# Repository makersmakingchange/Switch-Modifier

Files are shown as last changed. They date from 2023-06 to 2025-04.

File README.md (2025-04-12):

# Switch Modifier
## Overview

The switch modifier is an affordable accessibility device that enables specific switch output functions. With the provided Arduino code, the switch modifier outputs a momentary switch signal for a specific hold duration, in response to a digital input signal. Regardless of the duration of the input signal, the output can be set to any duration from 20 to 500 milliseconds. Manually turning a potentiometer allows for adjustment in output duration.

## Usage

With the provided Arduino code, the intended usage is for applications that require fast, short duration switch activation, where the user’s motor control is too slow to achieve such movement. To achieve multiple switch activations, the user must release the input switch first before activating it again. Minor adjustments to the code may provide for longer output durations, or latching functionality.

## Disclaimer
**Construction, use and modification of this device is the responsibility of the end user. The Stan Cassidy Centre for Rehabilitation and its employees are not responsible for any damages or harm as a result of the construction or use of this device.**

## Build Instructions

#### Tools Required

- Soldering Iron
- Screw Driver
- Wire Cutters / wire strippers
- Super Glue

#### 3D Printing

The lid and the base are printed face up with no supports. The middle piece is printed in its intended usage orientation (lettering upright) and will require supports in the bottom battery compartment, and port holes in the walls. The original box was printed on a Raise3D N2 printer using PLA. Speed printing is approximately 7.5 hours and high quality is approximately 18.5 hours.

### Assembling the Circuit

Take care in the placement of the electronics on the proto board to allow for everything to fit. Only attach the back end of the nano controller up to pins D2 and A7 (inclusive). The remaining portion of the controller will overhang and rest on the support structure. Ensure the nano controller will line up with the access port on the side wall of the 3D printed box.
Please refer to the following diagram for assembling the rest of the circuit.
Note: Do not solder the battery holder wires on until the 3D printed box is ready and the wires can be passed through the access hole.

### Assembling the Box

1. Remove all 3D printed supports from the middle section of the box.
2. Feed the battery holder wires through the access hole and mount it in the bottom compartment using two M2x6 screws.
3. Mount the assembled proto board to the standoffs in the upper compartment using two M2x6 screws.
4. Solder the battery wires to the appropriate locations on the proto board. Ensure not to melt the plastic box.
5. Mount the auxiliary mono jacks in the appropriate port holes in the walls of the box.
6. Mount the ON/OFF switch in the remaining port hole in the wall of the box using super glue. Ensure not to glue the switch stuck in the ON or OFF position.
7. Attach the lid of the box using four M2x20 screws. Ensure not to over torque the screws and damage the lid. Also, ensure that no wires are pinched between the lid and the walls of the box.
8. Insert four AA batteries (not included in list of materials) into the battery holder.
9. Attach the base of the box using found M2x20 screws. Ensure not to over torque the screws and damage the base.

## License
<!--- LICENSE Choose an appropriate license. We recommend an open-source hardware compatible license. --->
Everything needed or used to design, make, test, or prepare the Switch Modifier is licensed under the CERN 2.0 Weakly Reciprocal license <https://ohwr.org/project/cernohl/wikis/Documents/CERN-OHL-version-2> (CERN-OHL-W).

Accompanying material such as instruction manuals, videos, and other copyrightable works that are useful but not necessary to design, make, test, or prepare the Switch Modifier are published under a Creative Commons Attribution-ShareAlike 4.0 license <https://creativecommons.org/licenses/by-sa/4.0/> (CC BY-SA 4.0).

## Attribution 
<!--- ATTRIBUTION Include any information related to the development of the design. This may include who identified the initial challenge, who contributed to the design --->
The Lift Switch was designed by the Rehabilitation Engineering Department at Horizon Health's Stan Cassidy Centre for Rehabilitation (SCCR).  

The documentation template was created by Makers Making Change and is used under a CC BY-SA 4.0 license. It is available at the following link: https://github.com/makersmakingchange/OpenAT-Template

---

<!-- ABOUT MMC START -->
## About Makers Making Change
[Makers Making Change Logo](https://www.makersmakingchange.com/)

Makers Making Change is a program of [Neil Squire](https://www.neilsquire.ca/), a Canadian non-profit that uses technology, knowledge, and passion to empower people with disabilities.

Makers Making Change leverages the capacity of community based Makers, Disability Professionals and Volunteers to develop and deliver affordable Open Source Assistive Technologies.

 - Website: [www.MakersMakingChange.com](https://www.makersmakingchange.com/)
 - GitHub: [makersmakingchange](https://github.com/makersmakingchange)
 - Bluesky: [@makersmakingchange.bsky.social](https://bsky.app/profile/makersmakingchange.bsky.social)
 - Instagram: [@makersmakingchange](https://www.instagram.com/makersmakingchange)
 - Facebook: [makersmakechange](https://www.facebook.com/makersmakechange)
 - LinkedIn: [Neil Squire Society](https://www.linkedin.com/company/neil-squire-society/)
 - Thingiverse: [makersmakingchange](https://www.thingiverse.com/makersmakingchange/about)
 - Printables: [MakersMakingChange](https://www.printables.com/@MakersMakingChange)

### Contact Us
For technical questions, to get involved, or to share your experience we encourage you to [visit our website](https://www.makersmakingchange.com/) or [contact us](https://www.makersmakingchange.com/s/contact).
<!-- ABOUT MMC END -->

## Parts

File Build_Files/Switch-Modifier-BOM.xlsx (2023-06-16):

Switch Modifier BOM
Arduino Nano (elegoo) | 1 | 5.883333333 | 5.883333333 | https://www.amazon.ca/Arduino-ELEGOO-ATmega328P-Compatible-Without/dp/B071NMD14Y?hvadid=208380738475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
Aux ports | 2 | 1.68 | 3.36 | https://www.digikey.ca/products/en?keywords=CP1-3533NG-ND
Relays | 1 | 7.34 | 7.34 | https://www.digikey.ca/product-detail/en/omron-electronics-inc-emc-div/G6E-134P-ST-US-DC5/Z830-ND/127440?pcrid=267468162425&pkw=&pmt=b&pdv=c&productid=&slid=
3D printed box (PLA) | 1 | 3 | 3 | Rehab Eng Supplies
Wires/Solder/Heat shrink | 1 | 0.5 | 0.5 | Misc supplies
Battery Holder 4xAA | 1 | 2.55 | 2.55 | https://www.digikey.ca/product-detail/en/keystone-electronics/2478/36-2478-ND/303823
SPST Switch | 1 | 1.65 | 1.65 | https://www.digikey.ca/product-detail/en/cw-industries/GF-123-3011/CWI334-ND/4089772
Fuse Holder | 1 | 0.95 | 0.95 | https://www.digikey.ca/product-detail/en/keystone-electronics/4527/36-4527-ND/8397
Fuse 250 mA | 1 | 0.3 | 0.3 | https://www.digikey.ca/product-detail/en/bel-fuse-inc/5MF-250-R/507-1257-ND/1009029
Project Board | 1 | 4.22 | 4.22 | https://www.digikey.ca/product-detail/en/adafruit-industries-llc/1608/1528-1101-ND/5154676
10kOhm Resistor | 1 | 0.15 | 0.15 | https://www.digikey.ca/product-detail/en/stackpole-electronics-inc/CF14JT10K0/CF14JT10K0CT-ND/1830374
Potentiometer | 1 | 0.57 | 0.57 | https://www.digikey.ca/product-detail/en/panasonic-electronic-components/EVN-DJAA03B55/DJA55CT-ND/274655
M2*6 Machine Screw | 4 | 0.06 | 0.24 | https://www.mcmaster.com/machine-screws
M2*20 Maching Screw | 4 | 0.06 | 0.24 | https://www.mcmaster.com/machine-screws
 |  |  | 30.95333333
Notes:
You can by a kit of small machine screws on amazon instead of individual sizes.
I used glue to mount the SPST ON/OFF switch.

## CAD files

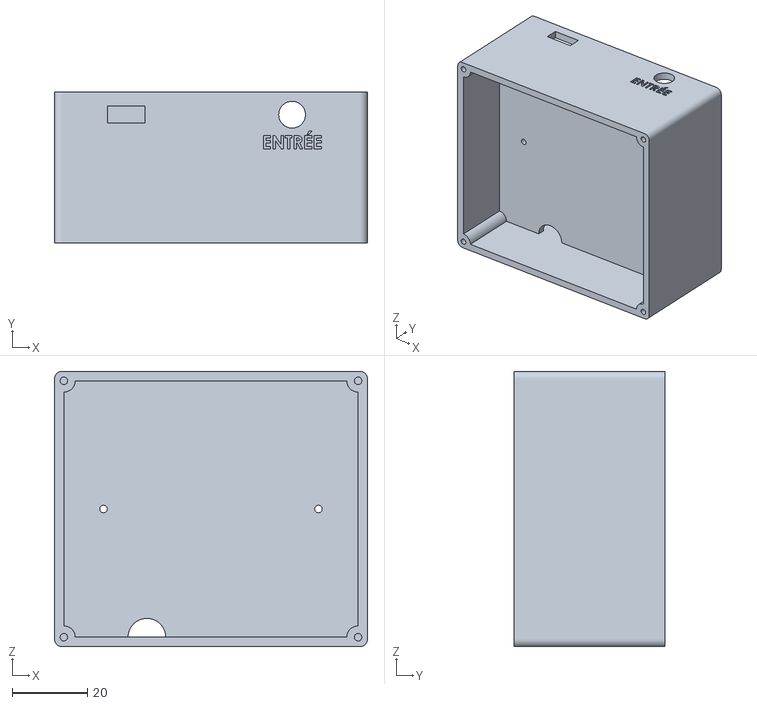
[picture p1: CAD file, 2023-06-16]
Build_Files/Electronics-Box-Switch-Modifier.STL
83.0 x 40.0 x 73.0

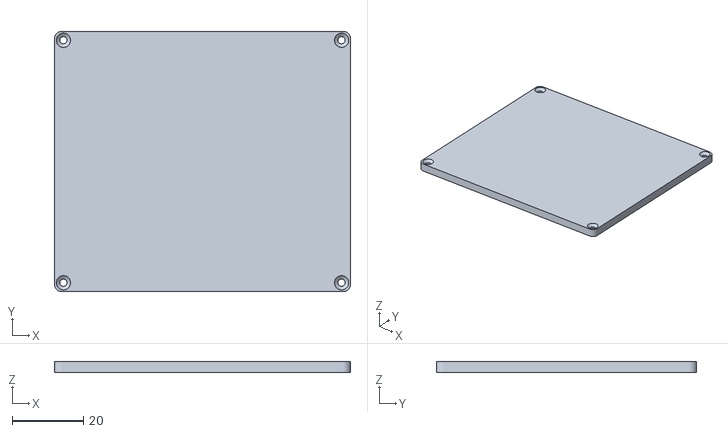
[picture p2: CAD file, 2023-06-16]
Build_Files/Base-Electronics-Box-Switch-Modifier.STL
83.0 x 73.0 x 3.00

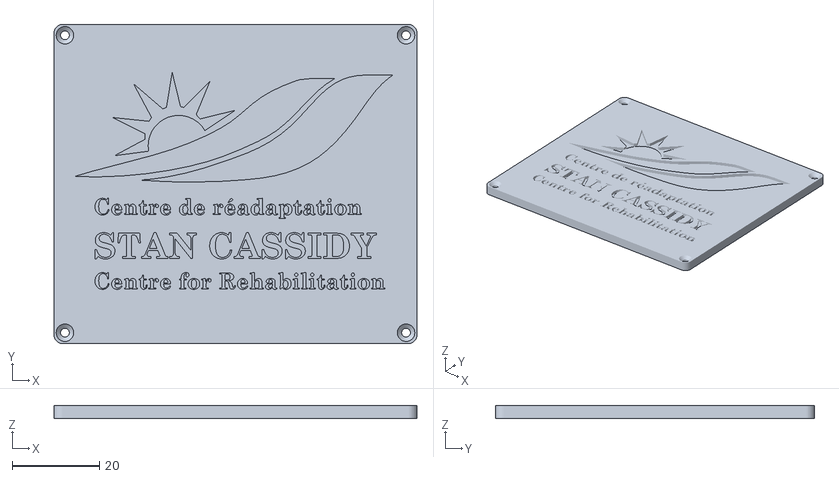
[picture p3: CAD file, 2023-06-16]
Build_Files/Lid-Electronics-Box-Switch-Modifier.STL
83.0 x 73.0 x 3.00

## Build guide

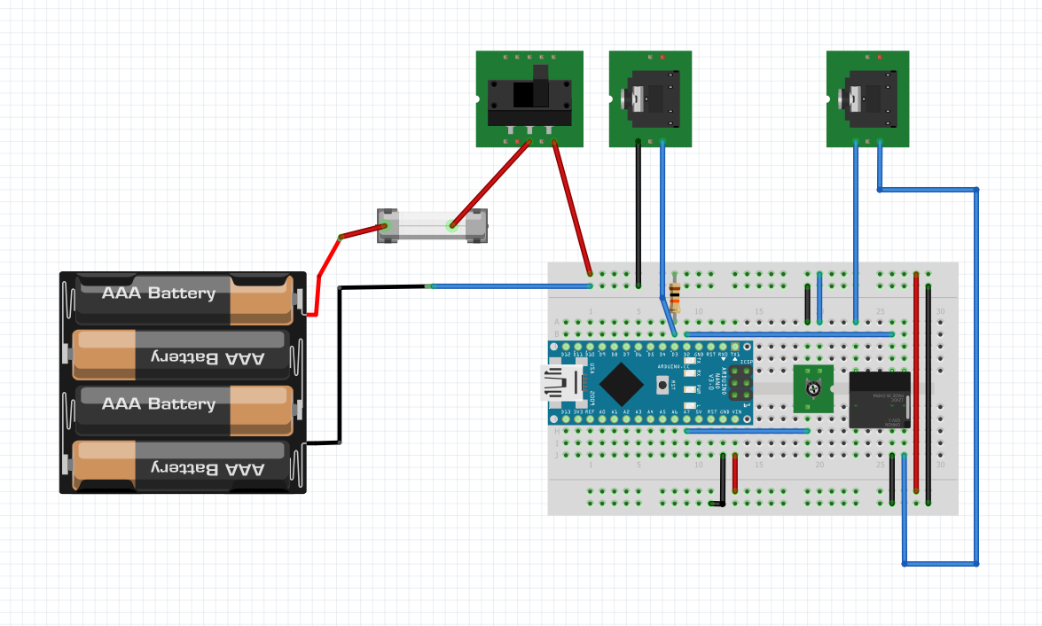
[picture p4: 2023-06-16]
Build_Files/Switch-Modifier Circuit Diagram.png

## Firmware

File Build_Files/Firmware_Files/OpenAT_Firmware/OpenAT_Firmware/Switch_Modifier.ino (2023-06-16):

// Switch Modifier
// Created by Rachelle Bernier
// Stan Cassidy Centre for Rehabilitation, Rehabilitation Engineering Department
// September 2019


unsigned long potPin = A7; //potentiometer input
unsigned long enterPin = 3; //digital input signal
unsigned long exitPin = 2; //digital output signal
int temp; //temporary placeholder for analog input value from potentiometer
int holdTime; //output momentary signal duration
boolean flag = 0; //identifier to ensure user releases input before another activation can be completed


void setup() {
  pinMode(potPin, INPUT);
  pinMode(enterPin, INPUT_PULLUP);
  pinMode(exitPin, OUTPUT);
  digitalWrite(exitPin, LOW);
  //Serial.begin(9600); //uncomment for testing purposes
  delay(500);
}
void loop() {

// SECTION A: The following section of code sets a threshold for a momentary output signal duration given the input from the potentiometer.
  temp = analogRead(potPin);
  holdTime = map(temp, 0, 920, 20, 500);
  
  //Serial.println(holdTime); //uncomment for testing purposes
  if ((digitalRead(enterPin) == LOW) && flag == 0) {
    flag = 1;
    digitalWrite(exitPin, HIGH);
    delay(holdTime);
    digitalWrite(exitPin, LOW);
  }
  
  if (digitalRead(enterPin) == HIGH)
  {
  flag = 0;
  }
///////////////////////////////////////////////////////////////////////////////////////////////////////////
// SECTION B: The following section of code sets the switch modifier to latching mode. Comment out section A if you would like the modifier to be in latching mode.
// if ((digitalRead(enterPin) == LOW) && flag == 0) {
//  flag = 1;
//  digitalWrite(exitPin, HIGH);
// }
// if ((digitalRead(enterPin) == LOW) && flag == 1) {
//  flag = 0;
//  digitalWrite(exitPin, LOW);
// }
//////////////////////////////////////////////////////////////////////////////////////////////////////////
}
